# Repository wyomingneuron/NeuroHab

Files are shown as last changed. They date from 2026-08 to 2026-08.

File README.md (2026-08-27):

# QUICK START GUIDE
This README contains the documentation for setup, addresses FAQ's, hardware installation, calibration, and more. Generally after a new problem is solved it is documented here.<br>
Check for solutions here and if this README does not solve your problem email me, Samuel Crouse at scrouse2@uwyo.edu.<br><br>

Latencies for the builds found here are <1ms with maxes at ~700 microseconds for 3 Lickport setups. Manuscipt latencies apply except for HTML versions whose latencies are slightly increased for the FED3 only (56->~150us).

## Setup Options
Both options require the dependencies below.
#### Option 1 - Standard Arduino .ino Control - Default - NeuroHab_firm
Provides nuanced system control based on C++ programmed control scripts.
Flash NeuroHab_firm scripts and program the desired "-MEGA_program_name" for your paradigm. <br><br>

Brief setup guide:
1. Flash the Arduino MEGA with NeuroHab-MEGA_Example (or your desired paradigm)
2. Flash the FED3 with the NeuroHab_Classic.ino
3. Flash the ESP32 with NeuroHab-ESP_Logging.ino
4. Complete the "NeuroHab Checklist ReadMe.md"

#### Option 2 - Desktop Arduino HTML Control - User Friendly - NeuroHab Desktop Control
Easily connect, operate, flash, and monitor experiments using the NeuroHab HTML Google Chrome script.
Provides a GUI interface for connecting COM ports and a block programming GUI for simple paradigms.
This is the easiest way to get started with the NeuroHab but lacks the finite paradigm control of Option 1. <br><br>

Brief setup guide:
1. Flash the Arduino MEGA with NeuroHab-MEGA-Desktop-V1.ino
2. Flash the FED3 with the FED3-Desktop-V1.ino
3. Flash the ESP32 with the NeuroHab-ESP_Logging.ino
4. Complete the "NeuroHab Checklist ReadMe.md"

#### Read the Experiment_README.md and the NeuroHab Checklist ReadMe.md for more information on the broad architecture.

## ARDUINO IDE DEPENDENCIES
FED3 by Lex Kravitz : 1.16.3<br>
CapacitiveSensor by Paul Bagder : 0.5.1<br>
LiquidCrystal_I2C Martin Kubovcik : 2.0<br>
ESP32 Espressif : 3.3.7<br>
Adafruit SAMD Boards : Arduino Boards Manager<br>
UART CP210 drivers are installed. Via CP210x VCP Windows Installer. This allows the ESP32 to connect properly via USB. <br><br>

# NeuroHab Basic Setup and Use
## NeuroHab_firm
<b>NeuroHab_Lib</b> goes in your arduino library folder. Probably: "C:\Users\username\Documents\Arduino\libraries\PLACE_HERE"

<b>The following go in your sketches folder.</b> <br>

NeuroHab-ESP_Logging <br>
NeuroHab-ESP_Logging_Setclock <br>
NeuroHab-MEGA_Example <br>
NeuroHab-MEGA_basic_lick <br>
NeuroHab-MEGA_flush_lines <br><br>

## Arduino IDE Board Selection
Files labeled -ESP will use <b>ESP32 Dev Module</b> <br>
Files labeled -MEGA will use <b>Arduino Mega or Mega 2560</b> <br><br>

## Flashing ESP32
Ensure UART CP210 drivers on installed. Via CP210x VCP Windows Installer. x64 installer <br><br>

## Flashing ESP32 Time Clock
Upload NeuroHab-ESP_Logging_Setclock to the Core to set the clock on the LCD screen. You MUST now reflash with NeuroHab-ESP_Logging.<br>
After selecting upload if the board does not automatically connect you made need to hold the boot button on the board. *The small button to the right of the micro-usb connection cable.<b><br><br>

## Flashing Arduino Mega 2560
Select the Arduino Mega 2560 COM6 (or COMX) from the drop down and select upload.<br><br>

## Removing Air Bubbles from Lines (flush lines)
To remove air bubbles from your lines you need to flash the Arduino Mega (lower square port) with <b>NeuroHab-MEGA_flush_lines</b>.<br>
By default this program will cycle open and closing each valve individually for 5 seconds. If this does not flush the lines properly, change the following lines of code.<br>

      if (valve == 1) {
          digitalWrite(VALVE_1, HIGH);
      }
      if (valve == 2) {
          digitalWrite(VALVE_2, HIGH);
      }
      if (valve == 3) {
          digitalWrite(VALVE_3, HIGH);
      }

      to

      if (valve == 1) {
          digitalWrite(VALVE_1, HIGH);
      }
      if (valve == 2) {
          digitalWrite(VALVE_1, HIGH);
      }
      if (valve == 3) {
          digitalWrite(VALVE_1, HIGH);
      }

Change VALVE_1 to VALVE_2 or VALVE_3 to flush each line completely. You must flash the Arduino each time you change the valve number.
#### You must reflash the Arduino with your desired code to resume experiment behavior.<br><br>

## Lickport Water Delivery Quantity Calibration
This code is found within "NeuroHab/NeuroHab_firm/NeuroHab_Lib/NeuroHab_Control.h" or locally "C:\Users\username\Documents\Arduino\libraries\NeuroHab_Lib\NeuroHab_Control.h"
One of the main limitations of the NeuroHab is the inability to communicate quantities between the Arduino MEGA controller and the ESP32 logger. This is overcome by hard coding the liquid delivery amount within:<br>

      NeuroHab-ESP_logging at the line
      float WD_QTY=0.006667 * 0.65;  // ml per WD

      and

      libraries/NeuroHab_lib/NeuroHab_Control.h at the line
      float lickTime = (250 * 0.65) - PULSE_SEPAR_DELAY_MS;	// How long the lickport valve is open before closing. Pulse delay to account for pulse time while valve is open.

The lickTime variable dictates how long the port stays open upon activation. IE greater times deliver more liquid and short times less.<br>
WD_QTY is the quantity that is recorded in the logging system. 0.65 is the scalar used to adjust delivery amount without ruining calibration approximately. IE at 250 ms 0.006667 ml is delivered and we scale the delivery time and amount by 0.65 to reduce the delivery amount without having to recalibrate delivery.<br>

However, if you need to change the delivery amount I recommend recalibration and this is the method.

1. Set the lickTime to the estimated time delivery amount. (100ms is generally about right to get a medium sized droplet delivered.)
2. Use a micropipette to measure the size of the droplet. (You may also program or manually deliver 10-50-100-X droplets into a container to have a greater amount to more easily measure. Remember to divide by the total number to get the average delivery size.)
3. If you found that your delivery amount is 0.002ml per delivery, replace <b>float WD_QTY=0.006667 * 0.65;</b> with <b>float WD_QTY=0.002;</b>
4. The scalar 0.65 is not mandatory and may be removed on recalibration, but adding your scalar or replacing with 1.0 is a good way to easily change delivery amount without recalibration.
5. After recalibration with a 0.002ml delivery amount your final code lines may look like this:

Example:

      NeuroHab-ESP_logging at the line
      float WD_QTY=0.002 * 1.0;  // ml per WD

      and

      libraries/NeuroHab_lib/NeuroHab_Control.h at the line
      float lickTime = (85 * 1.0) - PULSE_SEPAR_DELAY_MS;	// How long the lickport valve is open before closing. Pulse delay to account for pulse time while valve is open.

#### PULSE_SEPAR_DELAY_MS should not be removed as that delay is added during logging and removing it here will actually inflate the time the valves are open. Similarly, the minimum time a valve may be open is the PULSE_SEPAR_DELAY_MS which by default is 60ms. This also caps the logging at ~16HZ. I do not recommend changing PULSE_SEPAR_DELAY_MS at reducing times may cause events to be missed.<br><br>

## Lickports Activating Multiple Times? Reduce Sensitivity Here.
This code is found within "NeuroHab/NeuroHab_firm/NeuroHab_Lib/NeuroHab_Control.h" or locally "C:\Users\username\Documents\Arduino\libraries\NeuroHab_Lib\NeuroHab_Control.h"
 <br>
At 20 this is quite sensitive. 25 is good, and 30 may be too restrictive for mice, but it works well when manually activating it with a finger. Please test this value in your own setup.

# Memory Management
## ESP32_Logging.ino
These two variables are responsible for the majority of the ESP32 memory management issues. Adjusting numPins down results in more memory but a loss of functionality across BNC channels.
buffer_size allows for higher recording frequencies at larger values but uses much more memory. 90 is about the max. For example, adjusting numPins to 2 and buffer_size to 180 will allow for much higher single channel recording frequencies at the expense of channels 3 and 4 recording.
const int numPins = 4;                // 4 provides for 3 channels of BNC IN recording, 3 for 2, 2 for 1, 1 for BOX only events.
const int buffer_size = 90;           // << DEPENDING ON BUFFER DATA TYPES 100 WILL CRASH SYSTEM // how many pulses/times we can store before buffer overflow occurs.         Default 90 prior FED3 total event logging.

# Hardware Installation
## Lickport Installation
Each of 3 lickports comes with the port and magnetic housing. The housing inner diameter is ~21mm and the holes are sized for 3mm screws.<br>
To install I recommend placing the magnetic housing on the wall of your homecage and marking both mounting holes and the center 21mm hole with a sharpie. Then, use a 3.5mm drill bit to drill the mounting holes and a 20mm saw bit or similar to drill the center hole. Use the provided screws to mount the lickport housing on the wall. The lickport itself should now easily fit through the wall and allow liquid delivery into the homecage on activation.<br><br>

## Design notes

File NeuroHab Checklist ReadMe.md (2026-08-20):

# NeuroHab Ready? — Startup Checklist

Pre-session checklist for bringing a NeuroHab rig online. Work through the sections in order.

---

## 1. Fluid Lines

- [ ] Flush lines until water dispenses
  - [ ] Calibrate lines if not done recently
- [ ] Fill reservoir back to **60 mL**

---

## 2. Cords Connected

- [ ] Arduino — USB B
- [ ] Arduino — 12 V barrel jack
- [ ] ESP32 — micro USB
- [ ] FED3 Aux connected to the **correct** NeuroHab
- [ ] External BNC I/O

---

## 3. Connect All Devices

### 3a. FED3 Setup

Choose the branch that matches your setup.

**If using HTML FED3:**

- [ ] Turn on the FED3
- [ ] Connect Adafruit, Feather M0, or associated COM in Desktop Control
- [ ] Flash the HTML paradigm

> **Prerequisite:** `FED3_Desktop_V1.ino` must be flashed first.

**Else, using Classic FED3:**

- [ ] Flash FED3 with **NeuroHab Classic** or the desired paradigm
- [ ] Ensure `src` `.cpp` screen updates are turned **off** in `run()`

### 3b. Test FED3

- [ ] Trigger an event — it should display on the NeuroHab LCD screen
- [ ] **Non-HTML FED3:** power cycle it (off, then on) to reset the log
- [ ] **HTML FED3:** leave it on, or you will have to reconnect and *Send & Run* again

### 3c. COM Ports in Desktop Control (HTML Chrome Screen)

- [ ] Connect the **Arduino** COM port
  - Arduino (ATMEGA) — COM label reads `Arduino 2560` or similar
- [ ] Connect the **ESP32** COM port under *ESP32*
  - ESP32 — COM label reads `CP_UART…` or similar

---

## 4. SD Card

- [ ] SD card inserted
- [ ] `SD_CARD_ERROR` does **not** display on the NeuroHab LCD
- [ ] Display shows the current time

---

## 5. ESP32 and LEDs

- [ ] Reset the ESP32 once
- [ ] Confirm NeuroHab LEDs are **off**
  - If not: HTML → `ResetAll()` block → *Send & Run*
  - Then reset the ESP32 again

---

## 6. Run

- [ ] Import the desired NeuroHab HTML paradigm — **do not send it yet**
- [ ] Start External Data Collection - Sends Pulse to NeuroHab for Alignment
- [ ] *Send & Run* the NeuroHab HTML paradigm

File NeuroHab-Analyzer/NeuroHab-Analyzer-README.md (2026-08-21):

# NeuroHab-Analyzer

Python software for getting quick looks at your NeuroHab data. Python 3.11

#### DISCLAIMER
Much of this code is currently AI generated and unvalidated, please validate all findings separately and use this only as a tool for observation.

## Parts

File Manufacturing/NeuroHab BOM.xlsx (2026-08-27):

Item | QTY | Needed QTY | Cost | Needed Cost | Link | Cost for 1 Additional
Arduino Mega | 1 | 1.0 | $22.99 | $22.99 | link (https://www.amazon.com/ELEGOO-Compatible-Arduino-Projects-Compliant/dp/B01H4ZLZLQ) | $22.99 | Note* Check plumbing requirements before buying 1/16" or 3/16" tubing and barbs as some setups require both, 3/16", or 1/16".
ESP32 Dev Kit C | 3 | 1.0 | $15.99 | $5.33 | link (https://www.amazon.com/ESP-WROOM-32-Development-Microcontroller-Integrated-Compatible/dp/B08D5ZD528) | $0.00
BNC Female (Receiver) Right Angle 5pc | 5 | 5.0 | $10.99 | $10.99 | link (https://www.amazon.com/Superbat-Connector-Bulkhead-Monitoring-Transceiver/dp/B09V56M8F4?sp_csd=d2lkZ2V0TmFtZT1zcF9hdGY) | $10.99 |  | Item | QTY | Cost | Total Cost | Link
Replacement 22 AWG Wire | 1 | 0.1 | $15.69 | $1.57 | link (https://www.amazon.com/TUOFENG-Hookup-Wires-6-Different-Colored/dp/B0815ZDD5H?sp_csd=d2lkZ2V0TmFtZT1zcF9hdGY) | $0.00 |  | Arduino Mega | 3 | $22.99 | $68.97 | link (https://www.amazon.com/ELEGOO-Compatible-Arduino-Projects-Compliant/dp/B01H4ZLZLQ)
5V Relay Module Board 2pc | 2 | 1.0 | $9.99 | $5.00 | link (https://www.amazon.com/ANMBEST-Channel-Optocoupler-Expansion-Raspberry/dp/B08PP8HXVD) | $0.00 |  | ESP32 Dev Kit C | 1 | $15.99 | $15.99 | link (https://www.amazon.com/ESP-WROOM-32-Development-Microcontroller-Integrated-Compatible/dp/B08D5ZD528)
Good Solder | 1 | 0.01 | $5.99 | $0.06 | link (https://www.amazon.com/TOWOT-Purity-Electrical-Soldering-Content/dp/B09KM2LW4G?sp_csd=d2lkZ2V0TmFtZT1zcF9hdGY) | $0.00 |  | BNC Female (Receiver) Right Angle 5pc | 2 | $10.99 | $21.98 | link (https://www.amazon.com/Superbat-Connector-Bulkhead-Monitoring-Transceiver/dp/B09V56M8F4?sp_csd=d2lkZ2V0TmFtZT1zcF9hdGY)
LCD Screen IIC | 3 | 1.0 | $12.99 | $4.33 | link (https://www.amazon.com/Hosyond-Display-Module-Arduino-Raspberry/dp/B0BWTFN9WF?cv_ct_cx=lcd%2Bscreen%2B16x2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) | $0.00 |  | 5V Relay Module Board 2pc | 2 | $9.99 | $19.98 | link (https://www.amazon.com/ANMBEST-Channel-Optocoupler-Expansion-Raspberry/dp/B08PP8HXVD)
Micro SD Card Reader | 5 | 1.0 | $6.99 | $1.40 | link (https://www.amazon.com/HiLetgo-Adater-Interface-Conversion-Arduino/dp/B07BJ2P6X6) | $0.00 |  | LCD Screen IIC | 1 | $12.99 | $12.99 | link (https://www.amazon.com/Hosyond-Display-Module-Arduino-Raspberry/dp/B0BWTFN9WF?cv_ct_cx=lcd%2Bscreen%2B16x2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)
RTC Module DS3231 w Battery | 2 | 1.0 | $6.59 | $3.29 | link (https://www.amazon.com/AT24C32-Replace-Arduino-Batteries-Included/dp/B09LLMYBM1) | $0.00 |  | Micro SD Card Reader | 1 | $6.99 | $6.99 | link (https://www.amazon.com/HiLetgo-Adater-Interface-Conversion-Arduino/dp/B07BJ2P6X6)
Micro SD Cards 16GB | 10 | 1.0 | $33.39 | $3.34 | link (https://www.amazon.com/KEXIN-Adapter-microSDHC-Smartphone-Console/dp/B0D5H9YV1V) | $0.00 |  | RTC Module DS3231 w Battery | 2 | $6.59 | $13.18 | link (https://www.amazon.com/AT24C32-Replace-Arduino-Batteries-Included/dp/B09LLMYBM1)
Acrylic Sheets | 5 | 5.0 | $64.95 | $64.95 | link (https://www.amazon.com/Clear-Acrylic-Sheet-Plexiglass-Thick/dp/B07GLF88XP) | $64.95 |  | Food Grade PVC 1/16" Tubing | 1 | $24.99 | $24.99 | link (https://www.amazon.com/DERNORD-Tubing-Flexible-Clear-Vinyl/dp/B0D7CKLDM7?sp_csd=d2lkZ2V0TmFtZT1zcF9hdGY)
UF4007 Diodes | 125 | 5.0 | $5.99 | $0.24 | link (https://www.amazon.com/BOJACK-Recovery-UF4007-Electronic-Silicon/dp/B07Q6LLGKH?mcid=114b42586e3334d9a3b5288405fc546d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) | $0.00 |  | Food Grade PVC 3/16" Tubing | 1 | $21.99 | $21.99 | link (https://www.amazon.com/DERNORD-Tubing-Flexible-Clear-Vinyl/dp/B08NY3P85J?sp_csd=d2lkZ2V0TmFtZT1zcF9hdGY)
M3 Assortment | 40 | 8.0 | $5.99 | $1.20 | link (https://www.amazon.com/HELIFOUNER-Phillips-Screws-Kit-Stainless/dp/B0BV9CF62L?s=industrial) | $0.00 |  | Male Luer Lock 3/16" Tubing Barb | 1 | $7.99 | $7.99 | link (https://www.amazon.com/Syringe-Adapter-Male-Luer-Inch-Luer-Connector-Kit/dp/B0C1FV8NGL)
M4 Assortment | 40 | 2.0 | $5.99 | $0.30 | link (https://www.amazon.com/HELIFOUNER-Phillips-Screws-Kit-Stainless/dp/B0BV9PHCK1?s=industrial) | $0.00 |  | Valve to Luer 3/16" barb to 1/8" male | 1 | $7.99 | $7.99 | link (https://www.amazon.com/JoyTube-Plastic-Fittings-Adapter-Connector/dp/B08JD8LBHN?nsdOptOutParam=true&sp_csd=d2lkZ2V0TmFtZT1zcF9idGY)
FED3 | 1 | 1.0 | $650.00 | $650.00 | link (https://open-ephys.org/fed3/fed3) | $650.00 |  | 6mm Magnets | 1 | $9.99 | $9.99 | link (https://www.amazon.com/VSKIZ-Neodymium-Magnets-Multi-use-Whiteboard/dp/B0CZ71S57Y)
Insulated Alligator Clips | 20 | 3.0 | $7.88 | $1.18 | link (https://www.amazon.com/QMseller-Alligator-Insulated-Covered-Clamp/dp/B08MX7GXZ8?sp_csd=d2lkZ2V0TmFtZT1zcF9hdGY) | $0.00 |  | Aux to Wire | 1 | $8.99 | $8.99 | link (https://www.amazon.com/RIIEYOCA-Stereo-Equipment-Installed-Replace/dp/B09Y1BWKB5?sp_csd=d2lkZ2V0TmFtZT1zcF9hdGY)
30 ml Syringe Barrels | 20 | 3.0 | $7.88 | $1.18 | link (https://www.amazon.com/Individual-Measurement-Scientific-Measuring-Applicator/dp/B0BZ4FR8K9?sp_csd=d2lkZ2V0TmFtZT1zcF9hdGY) | $0.00 |  | Barrel Plug | 2 | $9.99 | $19.98 | link (https://www.amazon.com/SmoTecQ-Adapter-Security-Printer-Electronics/dp/B077PW5JC3)
LEECO Solenoid Valves 12V | 3 | 3.0 | $210.00 | $210.00 | link (https://www.theleeco.com/industries/other/products/solenoid-valves/) | $210.00 |  | Micro - USB | 2 | $5.99 | $11.98 | link (https://www.amazon.com/Charging-Transfer-Android-Trustable-MYFON/dp/B098DW7485)
240 SMD Resistors 0603 | 100 | 9.0 | $38.00 | $3.42 | link (https://www.mouser.com/ProductDetail/Vishay/TNPW0603240RBYEA?qs=sGAEpiMZZMtlubZbdhIBIEIUoz1ZD8I0HR6qsOGOJFk%3D) | $0.00 |  | Dispensing Needles 14 GA | 1 | $8.99 | $8.99 | link (https://www.amazon.com/Syringe-Dispensing-Needles-Length-Interface/dp/B07DZC225B)
1K SMD Resistors 0603 | 100 | 1.0 | $0.57 | $0.01 | link (https://www.digikey.com/en/products/detail/stackpole-electronics-inc/RMCF0603FT1K00/1761077) | $0.00 |  | 12V US SOLID Valves | 1 | $12.47 | $12.47 | link (https://ussolid.com/products/u-s-solid-electric-solenoid-valve-1-8-12v-dc-solenoid-valve-plastic-nylon-body-normally-closed-nbr-seal-html?pr_prod_strat=e5_des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)
1M SMD Resistors 0603 | 100 | 3.0 | $15.00 | $0.45 | link (https://www.mouser.com/ProductDetail/YAGEO/AR0603FR-071ML?qs=tggtontpCXN3Ykm7Gt7Sqw%3D%3D) | $0.00 |  | 5 Pin CS Cables | 5 | $9.98 | $49.90 | link (https://www.amazon.com/dp/B0BV94GN8M?ref=fed_asin_title)
2.54mm Terminal Adapters | 50 | 6.0 | $14.99 | $1.80 | link (https://www.amazon.com/Molence-Terminal-Connector-Terminals-26-18AWG/dp/B09F6TC7RP) | $0.00 |  | SD Card Reader | 3 | $4.99 | $14.97 | link (https://www.amazon.com/Reader-Adapter-Camera-Memory-Wansurs/dp/B0B9QZ4W4Y?s=electronics)
12V US SOLID Valves | 1 | 3.0 | $12.47 | $37.41 | link (https://ussolid.com/products/u-s-solid-electric-solenoid-valve-1-8-12v-dc-solenoid-valve-plastic-nylon-body-normally-closed-nbr-seal-html?pr_prod_strat=e5_des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) | $37.41
Food Grade PVC 1/16" Tubing | 100 | 10.0 | $24.99 | $2.50 | link (https://www.amazon.com/DERNORD-Tubing-Flexible-Clear-Vinyl/dp/B0D7CKLDM7?sp_csd=d2lkZ2V0TmFtZT1zcF9hdGY) | $0.00 |  | Totals | 24 | $205.91 | $295.44
Food Grade PVC 3/16" Tubing | 100 | 2.0 | $21.99 | $0.44 | link (https://www.amazon.com/DERNORD-Tubing-Flexible-Clear-Vinyl/dp/B08NY3P85J?sp_csd=d2lkZ2V0TmFtZT1zcF9hdGY) | $0.00
Male Luer Lock 3/16" Tubing Barb | 30 | 6.0 | $7.99 | $1.60 | link (https://www.amazon.com/Syringe-Adapter-Male-Luer-Inch-Luer-Connector-Kit/dp/B0C1FV8NGL) | $0.00
Male Luer Lock 1/16" Tubing Barb | 30 | 3.0 | $8.79 | $0.88 | link (https://www.amazon.com/30pcs-Adapter-Clear-Connector-Coupler/dp/B0BQBPJ6FS?hvadid=695239314676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) | $0.00
Female Luer Lock 1/16" Tubing Barb | 30 | 3.0 | $7.79 | $0.78 | link (https://www.amazon.com/Syringe-Adapter-Clear-Female-Luer-Connector-Kit-Coupler/dp/B0BM9QPS3M) | $0.00
Valve to Luer 3/16" barb to 1/8" male | 6 | 6.0 | $7.99 | $7.99 | link (https://www.amazon.com/JoyTube-Plastic-Fittings-Adapter-Connector/dp/B08JD8LBHN?nsdOptOutParam=true&sp_csd=d2lkZ2V0TmFtZT1zcF9idGY) | $7.99
Core / CS PCB | 5 | 1.0 | $60.23 | $12.05 | JLC PCB | $0.00
3D Print Structs | 4 | 4.0 | $2.00 | $2.00 |  | $2.00
3D Print Arms Long | 2 | 2.0 | $1.00 | $1.00 |  | $1.00
3D Print Arms Short | 1 | 1.0 | $1.00 | $1.00 |  | $1.00
3D Print Floor | 1 | 1.0 | $1.00 | $1.00 |  | $1.00
3D Print Brim | 1 | 1.0 | $1.00 | $1.00 |  | $1.00
3D Print Core | 1 | 1.0 | $6.00 | $6.00 |  | $6.00
6mm Magnets | 320 | 6.0 | $9.99 | $0.19 | link (https://www.amazon.com/VSKIZ-Neodymium-Magnets-Multi-use-Whiteboard/dp/B0CZ71S57Y) | $0.00
Aux to Wire | 4 | 1.0 | $8.99 | $2.25 | link (https://www.amazon.com/RIIEYOCA-Stereo-Equipment-Installed-Replace/dp/B09Y1BWKB5?sp_csd=d2lkZ2V0TmFtZT1zcF9hdGY) | $0.00
Barrel Plug | 2 | 1.0 | $9.99 | $5.00 | link (https://www.amazon.com/SmoTecQ-Adapter-Security-Printer-Electronics/dp/B077PW5JC3) | $0.00
Micro - USB | 2 | 1.0 | $5.99 | $3.00 | link (https://www.amazon.com/Charging-Transfer-Android-Trustable-MYFON/dp/B098DW7485) | $0.00
Dispensing Needles 14 GA 1" | 100 | 3.0 | $8.99 | $0.27 | link (https://www.amazon.com/Syringe-Dispensing-Needles-Length-Interface/dp/B07DZC225B) | $0.00
5 Pin CS Cables | 2 | 3.0 | $9.98 | $14.97 | link (https://www.amazon.com/dp/B0BV94GN8M?ref=fed_asin_title) | $14.97
100 PCS 5mm RGB LED | 100 | 3.0 | $7.99 | $0.24 | link (https://www.amazon.com/OWOFYDR-Three-Color-diodes-Cathode-Transparent/dp/B09BJ44NKZ?sp_csd=d2lkZ2V0TmFtZT1zcF9hdGY) | $0.00
10 PCS Active Buzzer | 10 | 1.0 | $6.99 | $0.70 | link (https://www.amazon.com/mxuteuk-Electronic-Computers-Printers-Components/dp/B07VK1GJ9X) | $0.00
Totals | 1489 | 124.1 | $1401.99 | $1095.27 |  | $1031.30
Totals - FED3 | 1488 | 123.1 | $751.99 | $445.27 |  | $381.30
Totals -Solenoids | 1486 | 121.1 | $1191.99 | $885.27 |  | $821.30
Totals - FED3 - Solenoids | 1485 | 120.1 | $541.99 | $235.27 |  | $171.30 | FED3 % of Total Cost | LEECO Valves % of Total Cost
Totals - Core Only with US Solenoids | 1480 | 115.1 | $477.04 | $170.32 |  | $106.35 | $650.00 | $210.00 |  | 1030 | 12.85726696
*Shipping costs may inflate price. Might be worth buying from Cole-Parmer to reduce plumbing costs. |  |  |  |  |  |  | 0.463626702 | 0.1497870884 | 0.6134137904
 |  |  |  |  |  |  | $993.89
Old
Smooth Bore Luer to 1/16" Tubing Barb | 10 | 3.0 | $10.00 | $3.00 | link (https://www.coleparmer.com/i/cole-parmer-luer-to-hose-barb-fitting-straight-adapter-white-nylon-cleanroom-packed-rotating-male-luer-lock-x-1-16-id-10-pk/50115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)

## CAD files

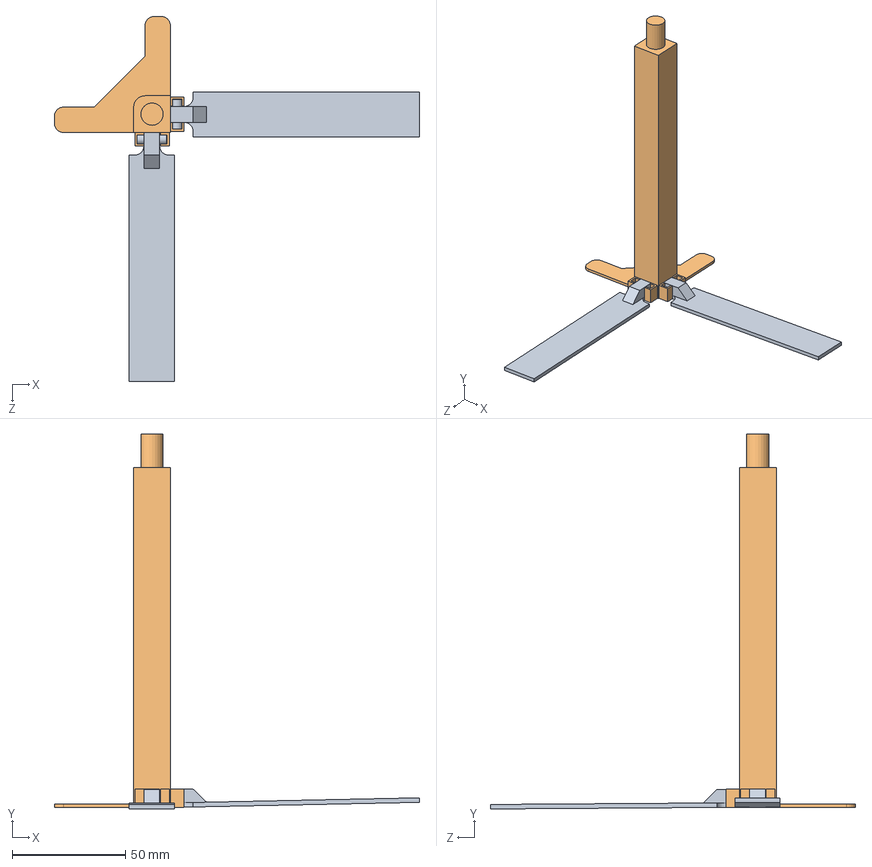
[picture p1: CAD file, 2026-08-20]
Manufacturing/CAD-3D Printing/sldprt/res holder standing/res holder standing asm.SLDASM
161.3 x 165.6 x 161.2 mm
res_holder_stand
res_holder_strut x 2

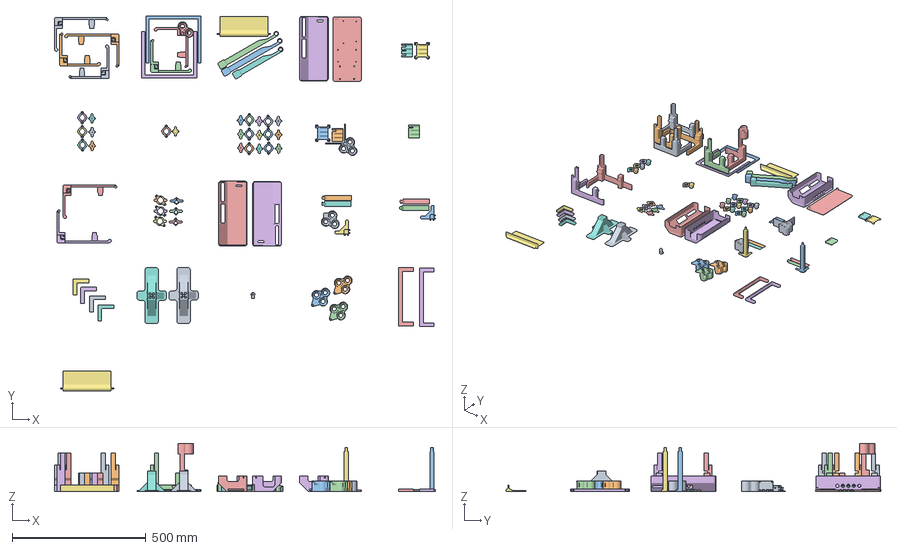
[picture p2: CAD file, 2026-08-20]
Manufacturing/CAD-3D Printing/3mf/NeuroHab-All.3mf
1427.8 x 1403.7 x 180.0 mm
corner_2_long.STL x 2
corner_3_long.STL x 2
floor_pan_long-1.STL x 2
corner_5.STL
corner_7.STL
FED3_stand.STL x 2
swingarm_short.STL
corner_2.STL
corner_3.STL
swingarm_long.STL x 2
control_box_lower_pcb.STL
control_box_upper_pcb.STL x 3
solenoid_holder_bottom.STL
solenoid_holder_top.STL
res_holder_magnetic.STL
solenoid_holder_top_2legacy.STL x 2
solenoid_holder_bottom_2legacy.STL
lickport male 4.STL x 13
lickport female 3.STL x 10
res_holder_stand.STL x 2
res_holder_strut.STL x 4
res_holder_top.STL
quarter rim.STL x 4
condstim_frame.STL x 3
condstim_housing.STL x 3
2020 Extrusion Gantry Cord Mount Whole.STL
res_holder_gantry.STL x 3
half rim.STL x 2
2020 Extrusion Stand.STL x 2

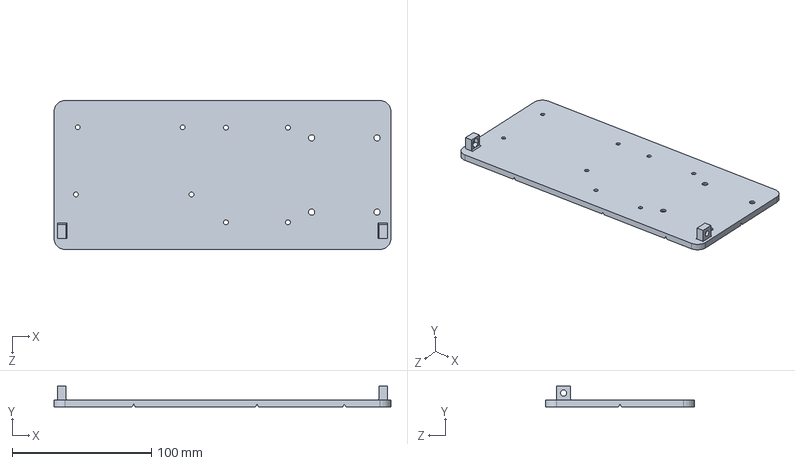
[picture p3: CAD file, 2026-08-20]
Manufacturing/CAD-3D Printing/sldprt/control_box_lower_pcb.SLDPRT
242.0 x 15.0 x 107.0 mm

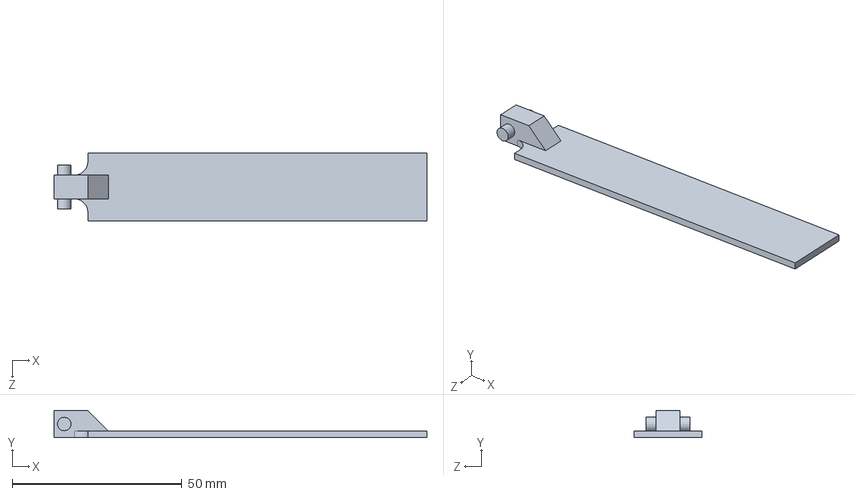
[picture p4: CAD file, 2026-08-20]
Manufacturing/CAD-3D Printing/sldprt/res holder standing/res_holder_strut.SLDPRT
110.0 x 8.00 x 20.0 mm

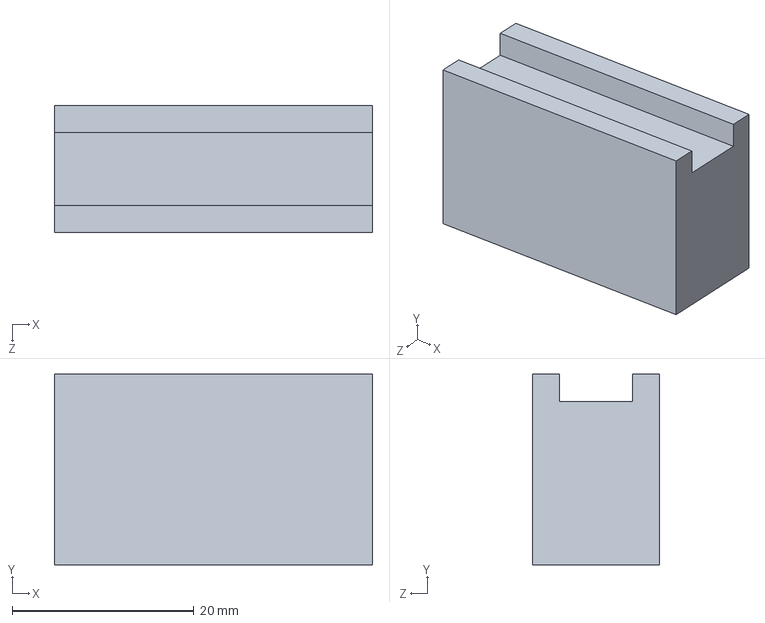
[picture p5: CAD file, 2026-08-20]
Manufacturing/CAD-3D Printing/sldprt/Wall Sliders/wall_slider_18mm.SLDPRT
35.0 x 21.0 x 14.0 mm

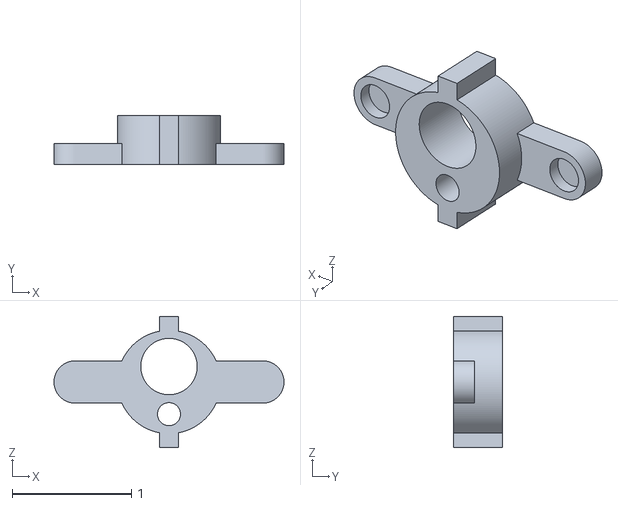
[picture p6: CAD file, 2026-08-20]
Manufacturing/CAD-3D Printing/stl/condstim_housing.STL
1.93 x 0.413 x 1.10

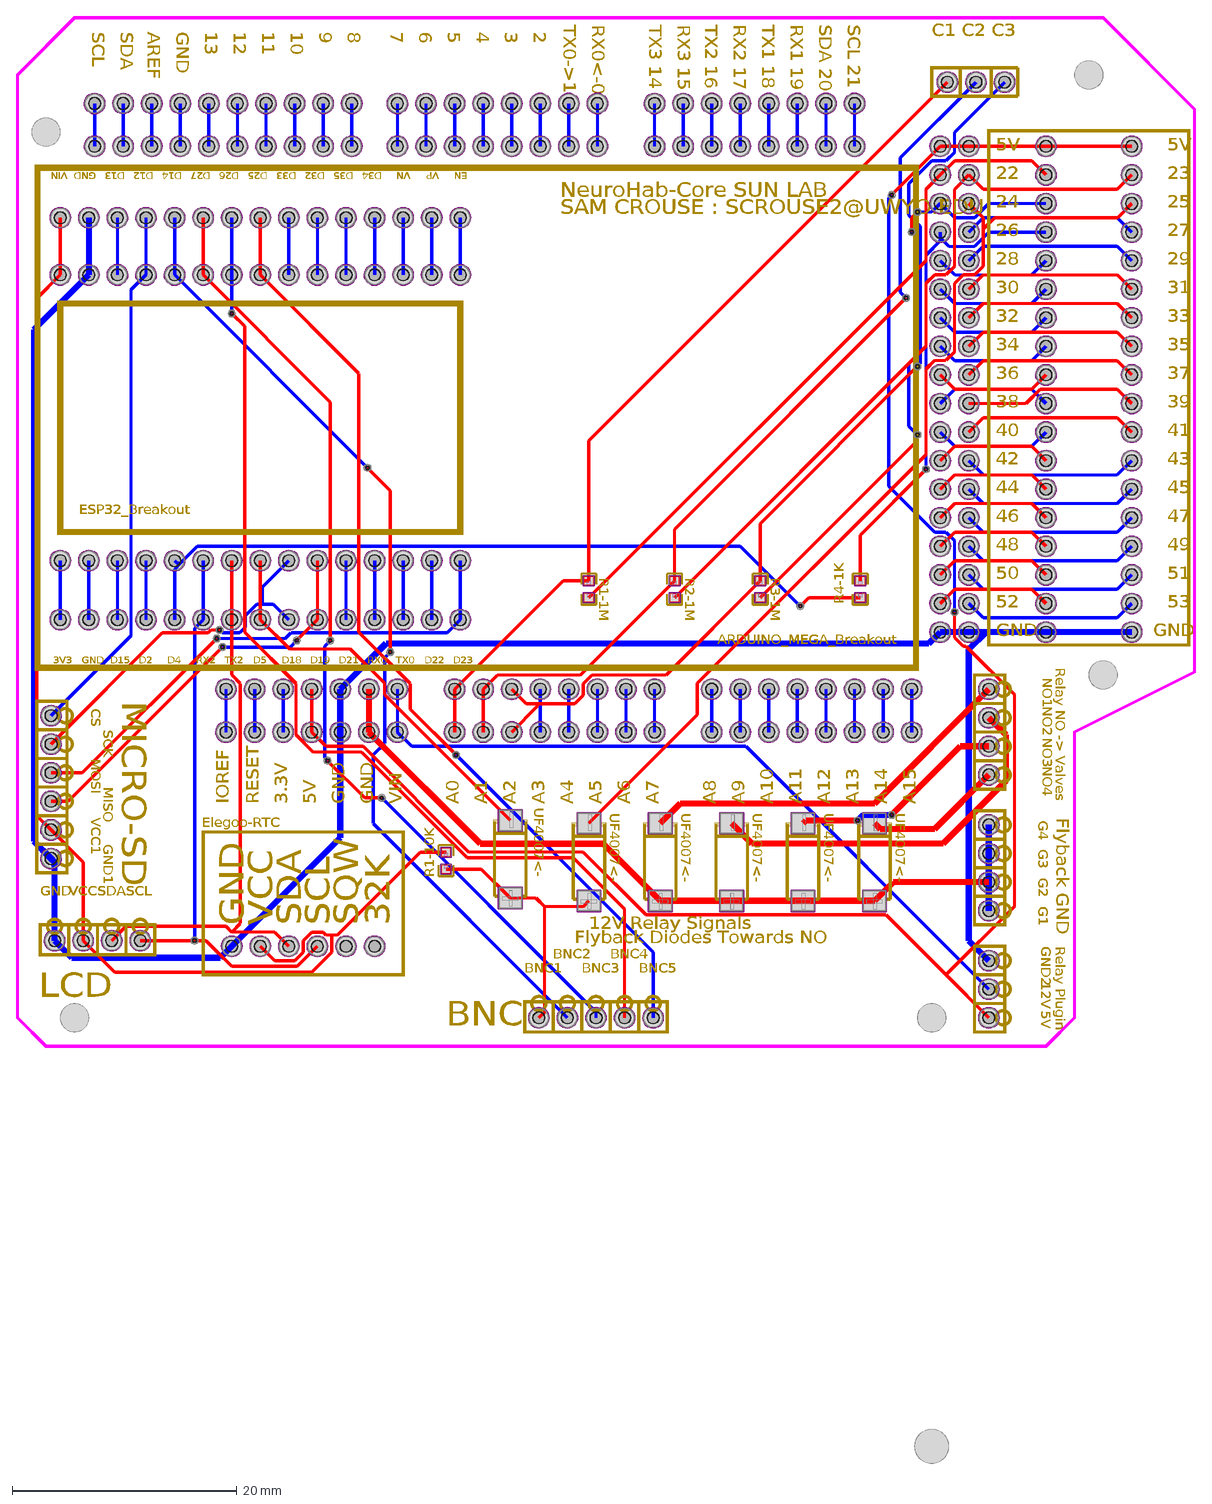
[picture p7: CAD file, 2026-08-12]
Manufacturing/Core PCB/NeuroHab PCB Core.dxf
LCD
MICRO-SD
BNC
12V Relay Signals
Flyback Diodes Towards NO
Flyback GND
Relay Plugin
Relay NO -> Valves
NeuroHab-Core SUN LAB
SAM CROUSE : SCROUSE2@UWYO.EDU
3V3
GND
D15
D2
D4
RX2
TX2
D5
D18
D19
D21
RX0
TX0
D22
D23
VP
VN
D34
D35
D32
D33
D25
D26
D27
D14
D12
D13
VIN
EN
ESP32_Breakout
C1 C2 C3
IOREF
RESET
3.3V
5V
A0
A1
A2
A3
A4
A5
A6
A7
A8
A9
A10
A11
A12
A13
A14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

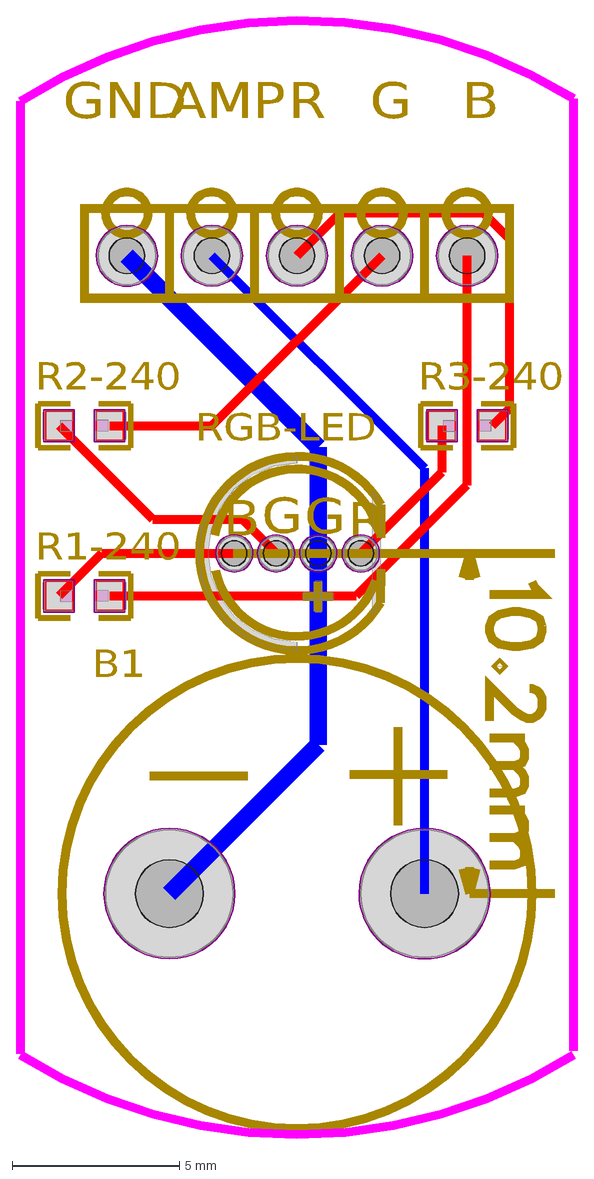
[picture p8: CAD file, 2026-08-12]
Manufacturing/CS Module PCB/NeuroHab CS Module PCB.dxf
B1
R1-240
R2-240
R3-240
B
G
R
RGB-LED
GND
AMP

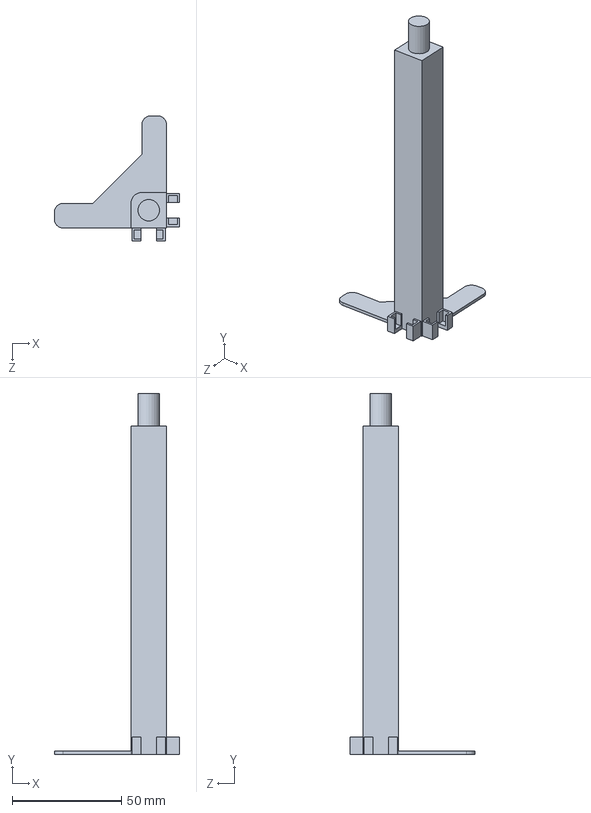
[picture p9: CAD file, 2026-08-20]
Manufacturing/CAD-3D Printing/sldprt/res holder standing/res_holder_stand.SLDPRT
57.2 x 164.9 x 57.2 mm

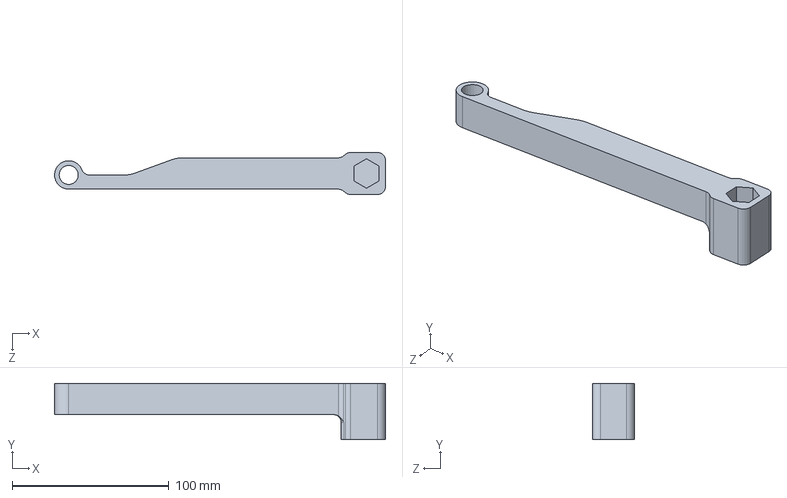
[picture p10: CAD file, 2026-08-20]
Manufacturing/CAD-3D Printing/sldprt/swingarm_short.SLDPRT
211.2 x 36.0 x 26.8 mm

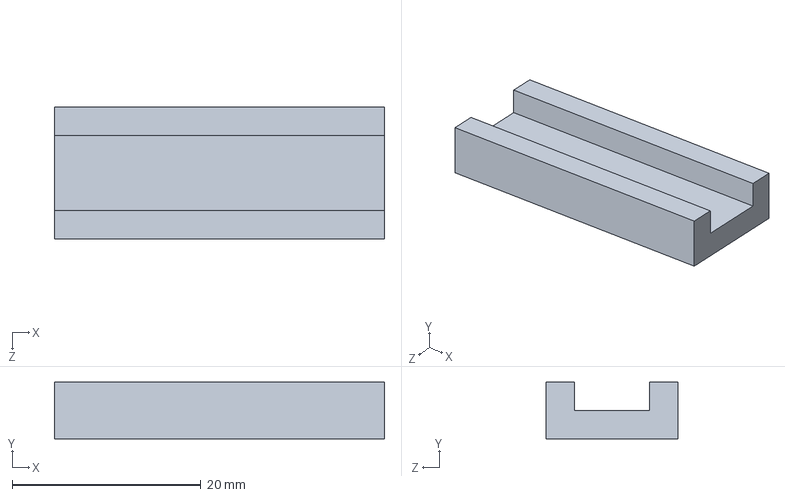
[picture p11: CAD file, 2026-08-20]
Manufacturing/CAD-3D Printing/sldprt/Wall Sliders/wall_slider_3mm.SLDPRT
35.0 x 6.00 x 14.0 mm

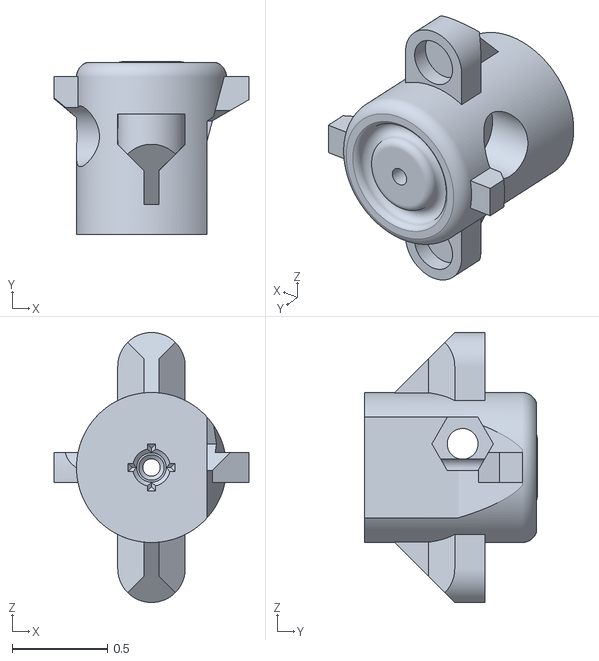
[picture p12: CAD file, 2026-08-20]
Manufacturing/CAD-3D Printing/stl/lickport male 4.STL
1.02 x 0.906 x 1.42

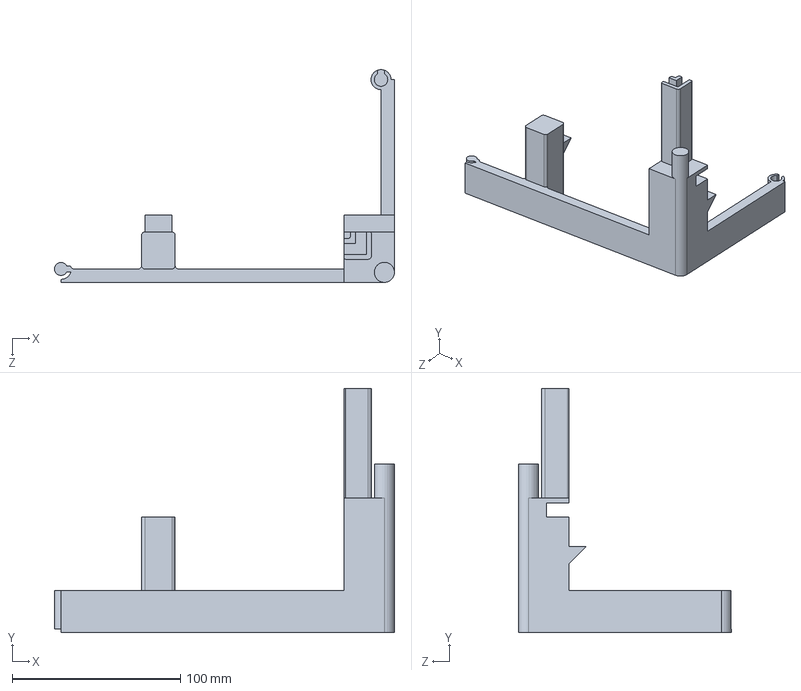
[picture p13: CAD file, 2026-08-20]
Manufacturing/CAD-3D Printing/sldprt/corner_2_long.SLDPRT
202.0 x 145.0 x 126.5 mm

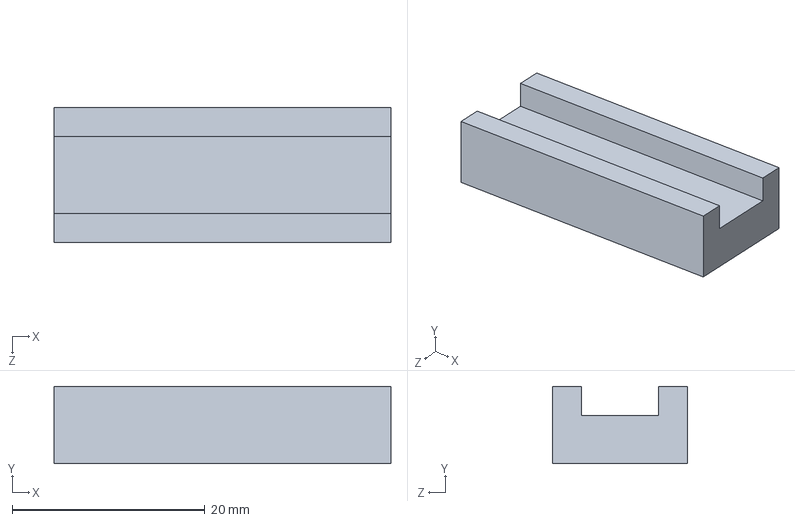
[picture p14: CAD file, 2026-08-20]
Manufacturing/CAD-3D Printing/sldprt/Wall Sliders/wall_slider_5mm.SLDPRT
35.0 x 8.00 x 14.0 mm

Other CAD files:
Manufacturing/CAD-3D Printing/sldprt/module 3 asm.SLDASM
Manufacturing/CAD-3D Printing/sldprt/asm control box pcb.SLDASM
Manufacturing/CAD-3D Printing/stl/half rim.STL
Manufacturing/CAD-3D Printing/sldprt/res holder standing/res_holder_gantry.SLDPRT
Manufacturing/CAD-3D Printing/sldprt/2020 Extrusion Stand.SLDPRT
Manufacturing/CAD-3D Printing/sldprt/FED3_stand.SLDPRT
Manufacturing/CAD-3D Printing/sldprt/Wall Sliders/stl/wall_slider_18mm.STL
Manufacturing/CAD-3D Printing/sldprt/Wall Sliders/stl/wall_slider_19mm.STL
Manufacturing/CAD-3D Printing/sldprt/Wall Sliders/stl/wall_slider_20mm.STL
Manufacturing/CAD-3D Printing/sldprt/Wall Sliders/stl/wall_slider_2mm.STL
Manufacturing/CAD-3D Printing/sldprt/Wall Sliders/stl/wall_slider_3mm.STL
Manufacturing/CAD-3D Printing/sldprt/Wall Sliders/stl/wall_slider_4mm.STL
Manufacturing/CAD-3D Printing/sldprt/Wall Sliders/stl/wall_slider_5mm.STL
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

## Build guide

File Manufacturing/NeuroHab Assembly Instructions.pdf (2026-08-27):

# Assembly & Wiring Instruction Sheet

This document organizes the build process into construction, soldering, and software installation stages. Use the checkboxes to track progress.

## 1. Construction / Printing & Assembly

1. Print core upper and lower components.
2. Print reservoir and back frames.
3. Print front extended or normal frames.
4. Print FED3 holder for frame.
5. Print 3× lickports / frames / CS frames.
6. Print floor pan (extended or normal).
7. Print swing arms.
8. Print acrylic rims.
9. Print solenoid holder.
10. Press-fit M3/M4 nuts into core frame. COMPLETE SOLDERING BEFORE CONTINUING
11. Install Arduino, relay, and solenoid frame onto core base plate using M3/M4 screws.
12. Install FED3 aux cable into GND / D5 screw terminals.
13. Plug 12-pin cable (3× 5-pin cables with each losing 1 pin to become 3× 4-pin cables) into CS PWM female connectors.
14. Install tubing from syringe barrels to middle of Leco solenoid, opposite terminal wire port, to lickport luer adapter.

## 2. Soldering / Wiring

1. Solder diodes and resistors (1k–1M ohm).
2. Solder Arduino pin connections (male).
3. Solder ESP32 pin connections (female).
4. Solder BNC, ESP32 D5, CS GND, lickport, relay, and relay-trigger screw terminals.
5. Solder Arduino CS PWM connections (female).
6. Solder Micro SD card, RTC, and LCD screen.

7. Tin 5 wires and solder onto BNC panel mount 1–5.
8. Tin 4 small wires and 1 long wire. Solder daisy-chain BNC grounds together and plug into core GND.
9. Solder all COM terminals together underneath relay module.
10. Tin and solder 5V, 1 GND, 3 signal wires, and install 5V, GND, 49, 51, and 53 to relay.
11. Tin 9 wires and solder from solenoid GND to PCB GND.
12. For remaining 6 wires, use 20 AWG. Twist one end together in parallel to create 3 wire sets with a 'V' connection. Solder one end to solenoid 12V and connect the V into relay NO. Connect remaining ends into Flyback 1, 2, or 3.
13. Tin one additional wire and attach from PCB 12V to COM4. (Power path: 12V → COM → NO (on signal) → Solenoid+ → Solenoid− → PCB GND. Flyback diode NO to GND.)
14. Solder 9× 240Ω resistors onto 3 CS module PCBs.
15. Solder 3× male 5-pin headers onto the back of the CS PCBs.
16. Solder 3× RGB LEDs onto front of CS module, ensuring orientation is correct.
17. Solder 3× buzzer onto front of CS module (5-pin).
18. For CS wiring: connect 3 shielded wires together at the male GND and extend to PCB GND. (Requires converting 5-pin to 4-pin by separating GND and creating space on PWM row.)

## 3. Software Installation

1. Flash ESP32 with ESP32 setclock / logging scripts (set clock, then reflash with logging).
2. Flash Arduino with required control script.

# Standalone Wiring Schematic

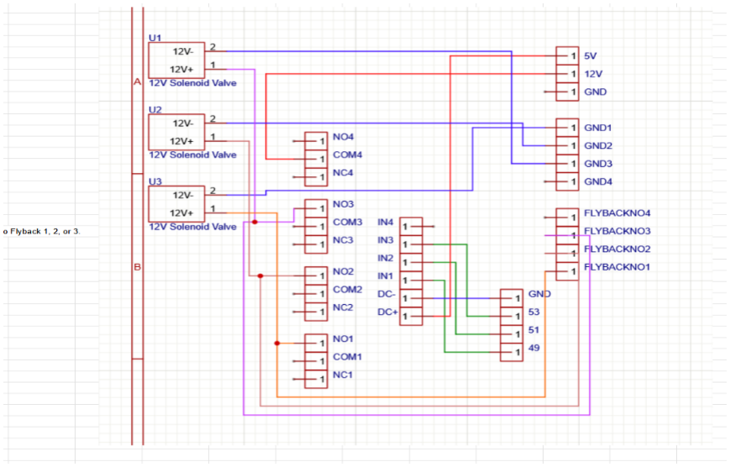
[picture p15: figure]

Reference schematic for relay, solenoid, flyback diode, and PCB wiring connections.

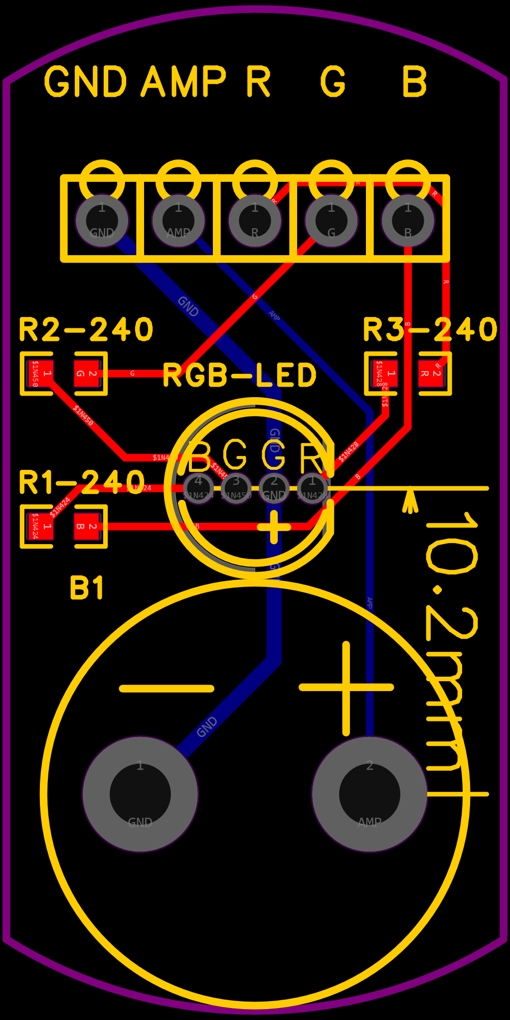
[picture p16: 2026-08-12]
Manufacturing/CS Module PCB/CS Module PCB Image.png

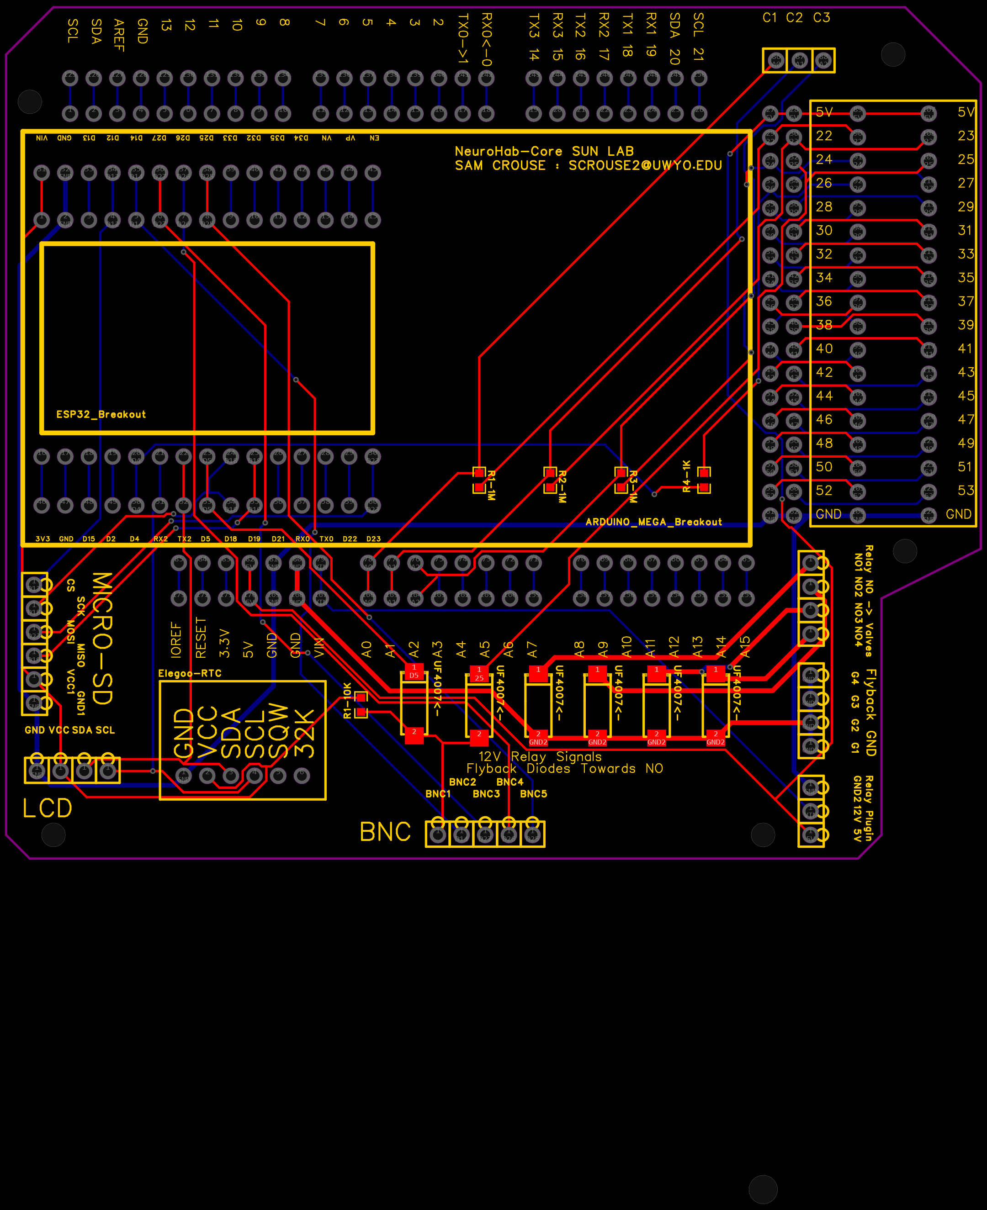
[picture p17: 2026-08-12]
Manufacturing/Core PCB/Core PCB Image.png

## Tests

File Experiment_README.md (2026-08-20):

# NeuroHab Training Documentation

## Overview

NeuroHab systems consist of three components:

| Component | Role |
|---|---|
| **Arduino MEGA** | Executes the experiment control flow — timing, variables, liquid delivery, conditioned stimulus, and logging requests. |
| **ESP32 DevModule** | Logs events based on TTL input. |
| **FED3 (Feather M0)** | Automated pellet feeding. |

---

## 1. Arduino MEGA

Executes the control flow of the experiment (timing, variables, liquid delivery, liquid conditioned stimulus, and initiating logging requests).

**Core library files** (place in the `NeuroHab_Lib` folder inside the Arduino Library):
- `NeuroHab_Control.h` — function instantiation and variable initialization
- `NeuroHab_Control.cpp` — function definitions

**Mutually exclusive sketches** (only one can be flashed onto the Arduino MEGA at a time):
- `NeuroHab-MEGA_basic_lick.ino` — simple basic licking script
- `NeuroHab-MEGA-Desktop-V1.ino` — HTML interface for visual scripting

---

## 2. ESP32 DevModule

Handles logging of events based on TTL input.

**Sketch to flash:**
- `NeuroHab-ESP_Logging.ino`

**BNC Ports** (numbered 1–5, right to left when facing the NeuroCore black box from the front):

| Port | Function |
|---|---|
| 1 | NeuroHab TTL Out — passthrough from Arduino pulsing |
| 2 | TTL Blank — customizable I/O port |
| 3–5 | BNC input to internal logging; timestamps aligned with NeuroHab microsecond time |

---

## 3. FED3 (Automated Pellet Feeding)

**Core library files** (replace the FED3 source defaults):
- `FED3.h`
- `FED3.cpp`

**Mutually exclusive sketches** (only one can be flashed onto the FED3 Feather M0 at a time):
- `NeuroHab_Classic.ino` — pretested basic FED3 programs
- `FED3-Desktop-V1.ino` — HTML interface for visual scripting

---

## Experiment Workflow

### Step 1 — Water Calibration Protocol

1. Open `NeuroHab_MEGA_calibrate_dispense.ino`.
2. Fill reservoir syringe barrels to the desired volume (recommended: 60 mL).
3. Place a preweighed tray under the FW port to catch dispensed liquid.
4. Flash `NeuroHab_MEGA_calibrate_dispense.ino` to the Arduino MEGA.
5. Edit the count dispensed in `Loop()` to dispense more or less.
   - Set this to the quantity you expect will be needed during the experiment. For example, if the mouse will drink ~3 mL, set the count to 100 — this lets you calibrate across a range of dispensed volumes for the best results.
6. Weigh the dispensed volume in grams.
7. Divide the measured volume by the total count dispensed (e.g., 100) to get the per-dispense volume in mL.
8. Set this calculated value as `WD_QTY` — for example: `WD_QTY = 0.02242;` — in:
   - `NeuroHab_Control.h` (open as `.txt`, edit `WD_QTY`, then save/close)
   - `NeuroHab-ESP_Logging.ino` (open in the Arduino IDE and edit `WD_QTY`)
9. Reflash the Arduino MEGA with the desired experiment code to update the internal value.
10. Reflash `NeuroHab-ESP_Logging.ino` with the new `WD_QTY`.

> **Optional — Validation:** Repeat steps 1–5 on a new NeuroHab file and verify that `totalWD_QTY` in `BNC_1` matches the weighed volume. It should be within 5%.

---

### Step 2 — NeuroHab to HTML Desktop Control: Setup

1. Open `NeuroHab_Desktop_Control_V1.html` (**Chrome required**).
2. Ensure `NeuroHab-MEGA-Desktop-V1` is flashed to the NeuroHab Arduino MEGA.
3. Ensure `NeuroHab-ESP_Logging` is flashed to the ESP32 DevModule.
   - `NeuroHab-ESP_Logging_Setclock` may be flashed first if the displayed clock is incorrect.
   - `NeuroHab_ESP_Logging_FP3002-MODIFIED` may be flashed in place of `NeuroHab-ESP_Logging.ino` if BNC Port 5 (for `BNC_4.csv`) needs to receive a single "high" start pulse.
4. Ensure `FED3-Desktop-V1` is flashed to the FED3, and that `src` `.h`/`.cpp` files are updated.

#### Important Dependencies

If COM ports do not appear or are incorrectly labeled for some devices, ensure the following are installed:
- Arduino IDE
- UART CP210 drivers (via the CP210x VCP Windows Installer)
- Adafruit SAMD Boards (via the Arduino Boards Manager)

#### Connecting Devices

1. In the NeuroHab Desktop Control **Devices** panel, navigate to **NeuroHab 1**. Find **ARDUINO** and select **Connect**.
2. Identify the COM port for the Arduino by plugging it in/out and waiting for the panel to update — or unplug other COM-port devices so only the Arduino is connected.
3. The Arduino is now connected.
4. Repeat the previous steps for the **ESP32** first, then the **FED3**.
5. Once all devices are connected, proceed to Experiment Execution.

---

### Step 3 — NeuroHab to HTML Desktop Control: Experiment Execution

1. Complete the HTML setup steps until all devices are connected.
2. Test device connections by pressing **Reset** in the Devices tab for the ESP32, and by uploading (**Send & Run** → **Selected NeuroHab**) simple stimulus LED scripts to the NeuroHab and FED3.
3. Design block programs or select one from the NeuroHab Program Library or FED3 Program Library.
   - NeuroHab and FED3 programs are block-scripted in separate windows.
4. Hit **Reset** on the ESP32 for the selected NeuroHab in the Devices tab. This resets the ESP32 and creates a new blank folder with `.csv` files.
5. Upload the FED3 program to the FED3 device by hitting **Send & Run**.
   - The FED3 must be powered on and **not** in bootloader mode.
6. Upload the NeuroHab program to NeuroHab 1, 2, 3, or **All Devices**.

> **Notes:**
> - Uploading serial communication to the NeuroHab may cause an erroneous RP (1 pulse) event — ignore this if it's the very first event.
> - The `millis` timestamp in `BNC_1` is based on the **ESP32 clock**, not the Arduino, and starts from ESP32 reset — not from **Send & Run**.

#### Concluding the Experiment

1. Select **Reset** on each active ESP32 device and verify the LCD screen on the NeuroHab Core turns off and opens a new file. Writing to the previous experiment file is now complete.
2. Select **Pause**, then upload the **Reset All** block in the Setup block-programming window to each NeuroHab to end execution of the existing paradigm.
3. Once events have ended, it is safe to remove the micro-SD card from the desired NeuroHab and evaluate the `.csv` files.

---

## Output File Reference

| File | Contents |
|---|---|
| `BNC_1.csv` | Experiment event data |
| `BNC_2.csv` – `BNC_4.csv` | BNC input event data, aligned with `BNC_1` (default) |

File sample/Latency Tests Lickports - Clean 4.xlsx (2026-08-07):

1 Sensor (n=200) | 2 Sensors (n=200) | 3 Sensors (n=200)
220 | 424 | 648
220 | 416 | 672
228 | 416 | 608
220 | 424 | 616
220 | 412 | 616
216 | 424 | 604
220 | 416 | 608
220 | 416 | 616
224 | 416 | 612
220 | 424 | 612
220 | 416 | 616
224 | 420 | 636
220 | 420 | 616
220 | 416 | 616
220 | 420 | 620
220 | 428 | 616
216 | 428 | 608
220 | 420 | 624
220 | 420 | 616
216 | 436 | 620
224 | 424 | 620
220 | 424 | 604
224 | 424 | 608
220 | 416 | 612
220 | 424 | 604
228 | 416 | 624
220 | 424 | 620
220 | 420 | 608
224 | 416 | 620
220 | 420 | 620
224 | 424 | 620
220 | 424 | 620
220 | 420 | 608
220 | 420 | 628
224 | 420 | 624
220 | 428 | 616
220 | 416 | 608
216 | 420 | 636
216 | 424 | 624
220 | 420 | 628
220 | 420 | 608
220 | 416 | 612
216 | 424 | 612
216 | 416 | 620
224 | 424 | 604
232 | 428 | 604
224 | 436 | 612
224 | 420 | 612
224 | 424 | 632
220 | 436 | 628
236 | 416 | 608
236 | 424 | 616
220 | 440 | 604
228 | 424 | 616
224 | 428 | 612
232 | 420 | 612
228 | 424 | 612
228 | 412 | 616
232 | 416 | 596
220 | 420 | 588
220 | 428 | 608
224 | 420 | 608
220 | 432 | 608
228 | 420 | 612
220 | 416 | 616
236 | 420 | 608
228 | 424 | 620
224 | 420 | 612
228 | 424 | 608
220 | 424 | 612
220 | 424 | 636
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

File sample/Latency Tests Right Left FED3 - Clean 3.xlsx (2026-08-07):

Left | Right
28 | 15
12 | 7
20 | 11
29 | 31
16 | 13
17 | 49
32 | 27
31 | 55
13 | 3
40 | 32
41 | 17
33 | 21
51 | 50
18 | 50
19 | 4
23 | 30
12 | 33
55 | 33
16 | 33
48 | 52
33 | 24
48 | 14
26 | 32
32 | 12
50 | 54
32 | 21
23 | 19
24 | 7
33 | 49
41 | 12
11 | 33
26 | 30
33 | 9
11 | 51
7 | 18
5 | 20
33 | 40
53 | 39
56 | 28
19 | 40
40 | 20
33 | 36
33 | 9
51 | 53
33 | 18
13 | 11
33 | 30
22 | 51
33 | 14
52 | 33
20 | 24
41 | 40
33 | 40
18 | 5
41 | 6
48 | 52
40 | 11
5 | 10
40 | 53
18 | 8
53 | 20
25 | 10
32 | 33
22 | 22
33 | 33
41 | 56
41 | 15
41 | 27
33 | 33
33 | 32
21 | 47
20 | 13
33 | 39
25 | 30
5 | 32
53 | 24
33 | 15
11 | 18
42 | 33
33 | 50
33 | 5
21 | 49
47 | 21
33 | 39
12 | 13
11 | 27
49 | 34
40 | 28
50 | 44
12 | 51
19 | 33
14 | 24
34 | 30
41 | 34
6 | 40
33 | 23
5 | 40
47 | 22
12 | 26
8 | 31

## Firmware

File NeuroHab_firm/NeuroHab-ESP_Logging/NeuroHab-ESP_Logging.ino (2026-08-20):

/*
AUTHOR: Sam Crouse
Email: scrouse2@uwyo.edu
Organization: Sun Lab Wyoming SBC
*/

// Libraries to include.
#include <LiquidCrystal_I2C.h>
#include <time.h>
#include <SdFat.h>
#include <SPI.h>
#include <RTClib.h>
#include <Wire.h>
#include <cstring>
#include <string>  // for double conversions and writing
#include <esp_timer.h>

RTC_DS1307 rtc;

// Initialize LCD
LiquidCrystal_I2C lcd(0x27, 16, 2);

// Pin definitions
#define PININ_1 5  // FED3 PULSING
#define PININ_2 4  // ARDUINO PULSING

#define SDA_PIN 17
#define SCL_PIN 16

#define SD_CS 12     // Chip Select
#define SPI_SCK 18   // Clock 18
#define SPI_MISO 19  // Master In Slave Out
#define SPI_MOSI 23  // Master Out Slave In 23

// global variables
// Read write variables.
char dirname[32];
String BNC_1_filename = "/BNC_1.csv";
String BNC_2_filename = "/BNC_2.csv";
String BNC_3_filename = "/BNC_3.csv";
String BNC_4_filename = "/BNC_4.csv";

SdFat SD;

int RP = 0;
int LP = 0;
int DISP = 0;
int RETR = 0;
int RW = 0;
int LW = 0;
int COND = 0;
int TONE = 0;
int FW = 0;
int WD = 0;
float RW_QTY = 0;
float LW_QTY = 0;
float FW_QTY = 0;
float WD_QTY = 0.0424875;  // ml per WD
float TWD_QTY = 0;               // total water delivered
int lastWaterPort = -1;          // 0 for RW, 1 for LW, 2 for FW

int RWP = 0;
int LWP = 0;
int RDD = 0;
int LDD = 0;
int RIT = 0;
int LIT = 0;

// screen variables
int mousePos = 15;

// timing variables
int screenMillis = 0;  // timestamp of last time we checked
int screenTimeout = 1000;
int clearMillis = 0;
int clearTimeout = 10000;

const int BATCH_WRITE_TIMEOUT_MICROS = 60000;  // << NEEDS TO BE GREATER THAN BOX_BNC_TIMEOUT_MICROS // The time required to elapse before buffers are switched if any buffer is not empty.
const int BOX_BNC_TIMEOUT_MICROS = 40000;      // << NEEDS TO BE LESS THAN BATCH_WRITE_TIMEOUT_MICROS and GREATER THAN BNC_TIMEOUT_MICROS // The pulse count timeout for NeuroHab events. If it takes longer than this to pulse
const int BNC_TIMEOUT_MICROS = 1000;           // << NEEDS TO BE SMALL BUT GREATER THAN MIN_PULSE_TIME_MICROS // The pulse count timeout for non-NeuroHab external BNC events.
const int MIN_PULSE_TIME_MICROS = 400;         // Error check value for how long a pulse must be to be considered a valid recordable pulse.

// pulse variables
volatile uint64_t init_pulse_time = -1;
volatile uint64_t last_pulse_time = 0;

// BNC / TTL INPUT VARIABLES
// Define input pins (ensure they support interrupts)
const int pulsePins[] = { PININ_1, PININ_2, 27, 26, 25 };  // Example GPIO pins // PININ_1 and PININ_2 are one output BNC for all NeuroHAB-AI events.
const int numPins = 4;                                     // 4 provides for 3 channels of BNC IN recording, 3 for 2, 2 for 1, 1 for BOX only events.

// Incoming pulses and times are stored and managed by the following variables and buffers (2D arrays).
const int buffer_size = 90;           // << DEPENDING ON BUFFER DATA TYPES 100 WILL CRASH SYSTEM // how many pulses/times we can store before buffer overflow occurs.         Default 90 prior FED3 total event logging.
const int a_b_switch_count_max = 60;  // << NEEDS TO BE LESS THAN buffer_size - RECOMMEND 49%-80% // How many values we store for writing before triggering buffer switching. Default 60 prior FED3 total event logging.
volatile int a_b_switch_count = 0;    // Tracks buffer increments.
volatile bool a_b_switch = false;     // When false, using _A vars for storage, when true using _B for storage. This tells us which buffer is our active buffer.

// volatile uint32_t pulseCounts[numPins] = {0};
volatile uint32_t pulseCounts_A[numPins][buffer_size] = { 0 };
volatile uint32_t pulseCounts_B[numPins][buffer_size] = { 0 };

// volatile uint64_t first_pulse_times[numPins] = {0};
volatile uint64_t first_pulse_times_A[numPins][buffer_size] = { 0 };
volatile uint64_t first_pulse_times_B[numPins][buffer_size] = { 0 };

// volatile uint64_t recent_pulse_times[numPins] = {0};
volatile uint64_t recent_pulse_times_A[numPins][buffer_size] = { 0 };
volatile uint64_t recent_pulse_times_B[numPins][buffer_size] = { 0 };

// Used to track if the most recent pulse times have been updated for each pin.
volatile uint64_t MRP_LAST_1 = 0;
volatile uint64_t MRP_LAST_2 = 0;
volatile uint64_t MRP_LAST_3 = 0;
volatile uint64_t MRP_LAST_4 = 0;

// volatile uint64_t latency_stamp_1 = 0;
// volatile uint64_t latency_stamp_2 = 0;

// Define a mutex for critical sections
portMUX_TYPE mux = portMUX_INITIALIZER_UNLOCKED;

// Interrupt Service Routines
// Access pulseCounts[0] for handlePulse0/1 because PININ_1 and PININ_2 share the output BNC port.

// BUILTIN BOX LICK EVENTS
void IRAM_ATTR handlePulse1() {
  uint64_t now_micros = esp_timer_get_time();

  const int pinNum = 0;

  if (a_b_switch == false) {
    // Get the index of the most recently set value in the array.
    int index = 0;
    for (int i = 0; i < buffer_size; i++) {
      if (pulseCounts_A[pinNum][i] == 0) {
        break;
      }

      index = i;
    }

    uint64_t most_recent_pulse = recent_pulse_times_A[pinNum][index];

    // Check if this pulse batch hasn't timed out.
    if (now_micros - most_recent_pulse < BOX_BNC_TIMEOUT_MICROS) {
      // Check the pulse was long enough to not be noise.
      if (now_micros - most_recent_pulse > MIN_PULSE_TIME_MICROS) {
        // If this is the first pulse in the batch, set the first pulse time.
        if (pulseCounts_A[pinNum][index] == 0) {
          first_pulse_times_A[pinNum][index] = now_micros;
        }

        pulseCounts_A[pinNum][index] += 1;
        recent_pulse_times_A[pinNum][index] = now_micros;
      }
    }

    // If this batch was timed out, increase the index and record the start of a new batch of pulses.
    else {
      // Check if the pulse was long enough to not be noise.
      if (now_micros - most_recent_pulse > MIN_PULSE_TIME_MICROS) {
        // ensure that the previous value had something written to it.
        if (pulseCounts_A[pinNum][index] != 0) {
          index += 1;
        }

        // If this is the first pulse in the batch, set the first pulse time.
        if (pulseCounts_A[pinNum][index] == 0) {
          first_pulse_times_A[pinNum][index] = now_micros;
        }

        pulseCounts_A[pinNum][index] += 1;
        recent_pulse_times_A[pinNum][index] = now_micros;
      }
    }
  }

  else {
    // Get the index of the most recently set value in the array.
    int index = 0;
    for (int i = 0; i < buffer_size; i++) {
      if (pulseCounts_B[pinNum][i] == 0) {
        break;
      }

      index = i;
    }

    uint64_t most_recent_pulse = recent_pulse_times_B[pinNum][index];

    // Check if this pulse batch has timed out.
    if (now_micros - most_recent_pulse < BOX_BNC_TIMEOUT_MICROS) {
      // Check the pulse was long enough to not be noise.
      if (now_micros - most_recent_pulse > MIN_PULSE_TIME_MICROS) {
        // If this is the first pulse in the batch, set the first pulse time.
        if (pulseCounts_B[pinNum][index] == 0) {
          first_pulse_times_B[pinNum][index] = now_micros;
        }

        pulseCounts_B[pinNum][index] += 1;
        recent_pulse_times_B[pinNum][index] = now_micros;
      }
    }

    // If this batch was timed out, increase the index and record the start of a new batch of pulses.
    else {
      // Check if the pulse was long enough to not be noise.
      if (now_micros - most_recent_pulse > MIN_PULSE_TIME_MICROS) {
        // ensure that the previous value had something written to it.
        if (pulseCounts_B[pinNum][index] != 0) {
          index += 1;
        }

        // If this is the first pulse in the batch, set the first pulse time.
        if (pulseCounts_B[pinNum][index] == 0) {
          first_pulse_times_B[pinNum][index] = now_micros;
        }

        pulseCounts_B[pinNum][index] += 1;
        recent_pulse_times_B[pinNum][index] = now_micros;
      }
    }
  }
}

// BNC IN PORT 3
void IRAM_ATTR handlePulse2() {
  uint64_t now_micros = esp_timer_get_time();

  const int pinNum = 1;

  if (a_b_switch == false) {
    // Get the index of the most recently set value in the array.
    int index = 0;
    for (int i = 0; i < buffer_size; i++) {
      if (pulseCounts_A[pinNum][i] == 0) {
        break;
      }

      index = i;
    }

    uint64_t most_recent_pulse = recent_pulse_times_A[pinNum][index];

    // Check if this pulse batch hasn't timed out.
    if (now_micros - most_recent_pulse < BNC_TIMEOUT_MICROS) {
      // Check the pulse was long enough to not be noise.
      if (now_micros - most_recent_pulse > MIN_PULSE_TIME_MICROS) {
        // If this is the first pulse in the batch, set the first pulse time.
        if (pulseCounts_A[pinNum][index] == 0) {
          first_pulse_times_A[pinNum][index] = now_micros;
        }

        pulseCounts_A[pinNum][index] += 1;
        recent_pulse_times_A[pinNum][index] = now_micros;
      }
    }

    // If this batch was timed out, increase the index and record the start of a new batch of pulses.
    else {
      // Check if the pulse was long enough to not be noise.
      if (now_micros - most_recent_pulse > MIN_PULSE_TIME_MICROS) {
        // ensure that the previous value had something written to it.
        if (pulseCounts_A[pinNum][index] != 0) {
          index += 1;
        }

        // If this is the first pulse in the batch, set the first pulse time.
        if (pulseCounts_A[pinNum][index] == 0) {
          first_pulse_times_A[pinNum][index] = now_micros;
        }

        pulseCounts_A[pinNum][index] += 1;
        recent_pulse_times_A[pinNum][index] = now_micros;
      }
    }
  }

  else {
    // Get the index of the most recently set value in the array.
    int index = 0;
    for (int i = 0; i < buffer_size; i++) {
      if (pulseCounts_B[pinNum][i] == 0) {
        break;
      }

      index = i;
    }

    uint64_t most_recent_pulse = recent_pulse_times_B[pinNum][index];

    // Check if this pulse batch has timed out.
    if (now_micros - most_recent_pulse < BNC_TIMEOUT_MICROS) {
      // Check the pulse was long enough to not be noise.
      if (now_micros - most_recent_pulse > MIN_PULSE_TIME_MICROS) {
        // If this is the first pulse in the batch, set the first pulse time.
        if (pulseCounts_B[pinNum][index] == 0) {
          first_pulse_times_B[pinNum][index] = now_micros;
        }

        pulseCounts_B[pinNum][index] += 1;
        recent_pulse_times_B[pinNum][index] = now_micros;
      }
    }

    // If this batch was timed out, increase the index and record the start of a new batch of pulses.
    else {
      // Check if the pulse was long enough to not be noise.
      if (now_micros - most_recent_pulse > MIN_PULSE_TIME_MICROS) {
        // ensure that the previous value had something written to it.
        if (pulseCounts_B[pinNum][index] != 0) {
          index += 1;
        }

        // If this is the first pulse in the batch, set the first pulse time.
        if (pulseCounts_B[pinNum][index] == 0) {
          first_pulse_times_B[pinNum][index] = now_micros;
        }

        pulseCounts_B[pinNum][index] += 1;
        recent_pulse_times_B[pinNum][index] = now_micros;
      }
    }
  }
}
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

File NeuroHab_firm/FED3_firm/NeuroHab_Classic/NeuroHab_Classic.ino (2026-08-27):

/*c:\Users\wjohnst6\Documents\Arduino\libraries\FED3\src\FED3.cpp
  Feeding experimentation device 3 (FED3)
  Classic FED3 script
  This script mimicks the classic FED3 menuing system for selecting among the following programs

  // FEDmodes:
  // 0 Free feeding
  // 1 FR1
  // 2 FR3
  // 3 FR5
  // 4 Progressive Ratio
  // 5 Extinction
  // 6 Light tracking FR1 task
  // 7 FR1 (reversed)
  // 8 PR (reversed)
  // 9 Optogenetic stimulation
  // 10 Optogenetic stimulation (reversed)
  // 11 Timed free feeding

  alexxai@wustl.edu
  December, 2020

  This project is released under the terms of the Creative Commons - Attribution - ShareAlike 3.0 license:
  human readable: https://creativecommons.org/licenses/by-sa/3.0/
  legal wording: https://creativecommons.org/licenses/by-sa/3.0/legalcode
  Copyright (c) 2020 Lex Kravitz

*/

#include <FED3.h>           //Include the FED3 library
String sketch = "Classic";  //Unique identifier text for each sketch
FED3 fed3(sketch);          //Start the FED3 object

/* ===========================================================================
   MODE -> PARADIGM
     0  Free_feed              6  Bellagio-48h
     1  DualPortTimed-Vegas    7  FR-Split-48h
     2  2x2Timed               8  RPR-Split-48h
     3  5x5TIMED               9  Medusa-48h
     4  ProgRatioTIMED        10  Sparrow-48h
     5  Dual_Port_Feeding     1
   =========================================================================== */

//////////////////////////
//variables for RPR tasks
int poke_num = 0;        // MODE 4 (ProgRatioTIMED) only
int pokes_required = 0;  // MODE 4 (ProgRatioTIMED) only
int left_pokes = 0;      // MODE 2 (2x2Timed) + MODE 3 (5x5TIMED)
int right_pokes = 5;     // MODE 2 (2x2Timed) + MODE 3 (5x5TIMED)
int upperbound = 11;     // MODE 4 (ProgRatioTIMED) only
///////////////////////////////////////////////////////
// Session timer variables (added for timer-based idle)
unsigned long sessionStart = 0;
const unsigned long SESSION_DURATION = 172800000;
// ^ IDLE LATCH: MODE 1 (Vegas), 2 (2x2Timed), 3 (5x5TIMED), 4 (ProgRatioTIMED),
//   9 (Medusa), 10 (Sparrow).  NOT 6 (Bellagio), 7 (FR-Split), 8 (RPR-Split).
bool isIdle = false;
bool isIdleLatch = false;
bool isProgRatio = false;  // MODE 4 (ProgRatioTIMED) only
////////////////////////////////////////////////////
// Variables for Double Poke and Double Poke Hold
float ran_range = 0;           // DEAD -- was MODE 10 (DP_Hold), replaced by Sparrow
float r1 = 1.0f;               // DEAD
float r2 = 3.0f;               // DEAD
unsigned long time_start = 0;  // DEAD
int poke_count = 0;            // DEAD

// NEW Bellagio /////////////////////////////////////////////////////////////////////////

unsigned long millis_start = 0;
const unsigned long timeout_time = 172800000;
// ^ MODE 6 (Bellagio), MODE 7 (FR-Split), MODE 8 (RPR-Split)

// NEW VEGAS FR ////////////////////////////////////////////////////////
// *** SHARED: MODE 6 (Bellagio, left port) AND MODE 7 (FR-Split, both ports) ***
int FR_init_count_right = 0;
int FR_init_limit_right = 5;  // MODE 7 (FR-Split) + MODE 11 (Bellagio-R)
int FR_init_count_left = 0;
int FR_init_limit_left = 5;  // MODE 6 (Bellagio) + MODE 7 (FR-Split)

int FR_req_right = 1;    // CHANGED 1->4. MODE 7 (FR-Split) + MODE 11 (Bellagio-R)
int FR_count_right = 0;  // MODE 7 (FR-Split) + MODE 11 (Bellagio-R)
int FR_req_left = 5;     // CHANGED 5->4. MODE 6 (Bellagio) + MODE 7 (FR-Split)
int FR_count_left = 0;   // MODE 6 (Bellagio) + MODE 7 (FR-Split)
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
